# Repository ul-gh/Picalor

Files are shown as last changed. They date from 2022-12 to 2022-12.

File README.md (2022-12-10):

# Picalor

## Multi-Channel Heat Balance Calorimetry on the Raspberry Pi
--> Incomplete - work-in-progress! <--

Thermal power (or heat flow) measurement of one segmented or multiple
individual liquid-cooled or liquid-heated systems under the assumption
that the enthalpy difference of the fluid entering and exiting each system
per unit of time is equal to the energy dissipated or released by the system.

Quasi-isothermal condition can be achieved by using a sufficiently high
flow rate. Accurate heat flow measurements under these conditions
require very sensitive and robust differential temperature sensing.

This is implemented by the Picalor hardware using platinum resistive
temperature sensors in a deflection-type bridge configuration connected
to a multi-channel, high-precision delta-sigma ADC system.

When performing the measurement with fluid temperatures set nearly at
environmental temperature level, convection and radiation heat loss
can be made negligible e.g. for power loss measurements in electronics.

For applications in chemistry, the multi-channel hardware can be useful
for Constant Flux Calorimetry or segmented Continuous Reaction Calorimters.

Supported hardware:

* Picalor OSHW Raspberry Pi add-on circuit board featuring:
    - 16-channel analog frontend for Pt 1000 sensors
    - 4x pulse-timing flow sensor inputs
    - 2x ADS1256 24-Bit 8-ch ADC
* Waveshare "High Precision AD/DA board"

## Hardware:
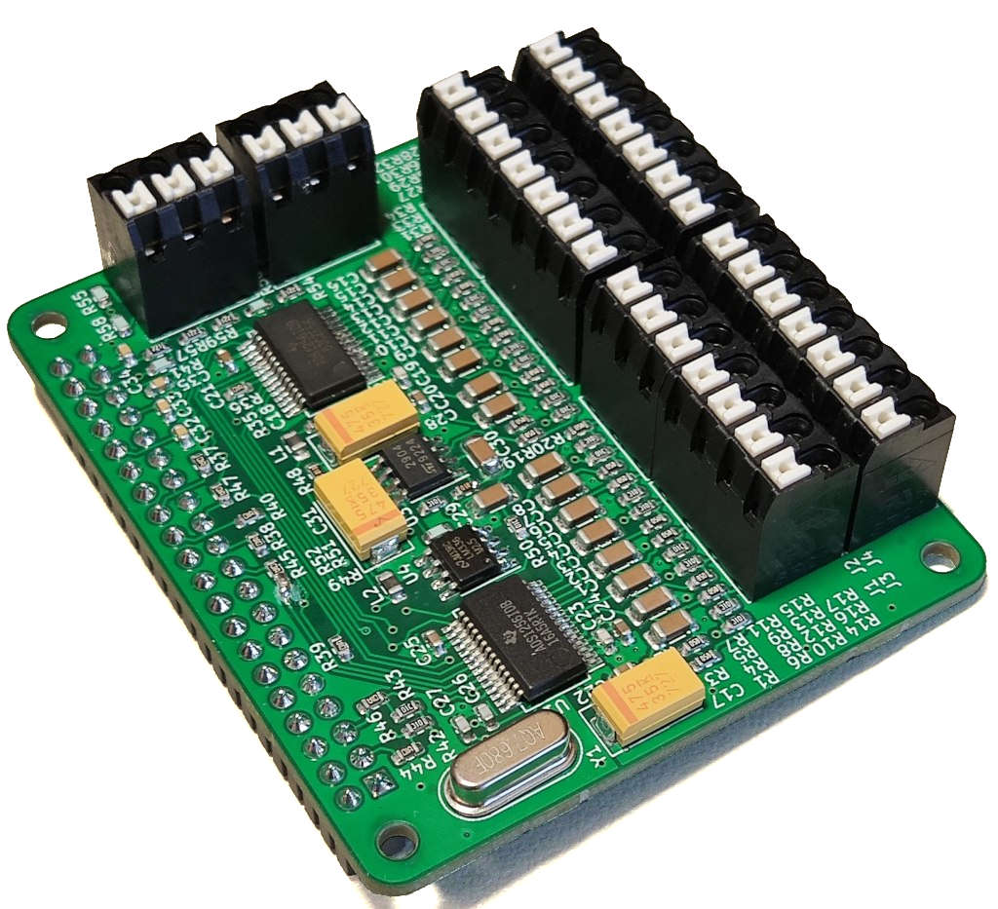
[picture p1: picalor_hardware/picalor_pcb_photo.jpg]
Picalor PCB Photo


* PCB Design Files: [picalor_hardware](picalor_hardware/)
* [Circuit Diagram (PDF)](https://ul-gh.github.io/Picalor/picalor_hardware/picalor_pcb.pdf)
* [Circuit BOM (HTML)](https://ul-gh.github.io/Picalor/picalor_hardware/ibom.html)

## Software Documentation (Generated):
* [Picalor Core (server component)](https://ul-gh.github.io/Picalor/picalor_core/html/namespaces.html)
* [Picalor App (browser client)](https://ul-gh.github.io/Picalor/picalor_app/html/files.html)

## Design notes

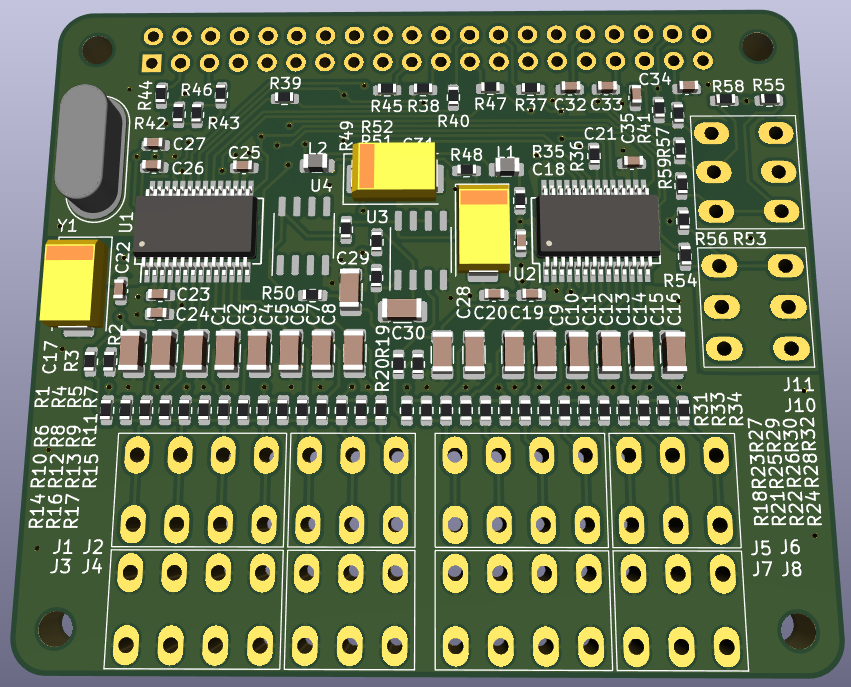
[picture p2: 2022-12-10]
picalor_hardware/circuit_schematics_pcb/picalor_3D_view.png

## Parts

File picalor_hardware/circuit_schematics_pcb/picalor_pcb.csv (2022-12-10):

Source: | D:\Bilanzkalorimeter\isoflux_pcb\isoflux_pcb\isoflux_pcb.kicad_sch
Date: | 18.05.2022 10:55:47
Tool: | Eeschema (6.0.5)
Generator: | C:\Program Files\KiCad\6.0\bin\scripting\plugins/bom_csv_grouped_by_value.py
Component Count: | 113
Individual Components:
Item | Qty | Reference(s) | Value | LibPart | Footprint | Datasheet
 |  | C1 | 1u | Device:C | Capacitor_SMD:C_1206_3216Metric | ~
 |  | C2 | 1u | Device:C | Capacitor_SMD:C_1206_3216Metric | ~
 |  | C3 | 1u | Device:C | Capacitor_SMD:C_1206_3216Metric | ~
 |  | C4 | 1u | Device:C | Capacitor_SMD:C_1206_3216Metric | ~
 |  | C5 | 1u | Device:C | Capacitor_SMD:C_1206_3216Metric | ~
 |  | C6 | 1u | Device:C | Capacitor_SMD:C_1206_3216Metric | ~
 |  | C7 | 1u | Device:C | Capacitor_SMD:C_1206_3216Metric | ~
 |  | C8 | 1u | Device:C | Capacitor_SMD:C_1206_3216Metric | ~
 |  | C9 | 1u | Device:C | Capacitor_SMD:C_1206_3216Metric | ~
 |  | C10 | 1u | Device:C | Capacitor_SMD:C_1206_3216Metric | ~
 |  | C11 | 1u | Device:C | Capacitor_SMD:C_1206_3216Metric | ~
 |  | C12 | 1u | Device:C | Capacitor_SMD:C_1206_3216Metric | ~
 |  | C13 | 1u | Device:C | Capacitor_SMD:C_1206_3216Metric | ~
 |  | C14 | 1u | Device:C | Capacitor_SMD:C_1206_3216Metric | ~
 |  | C15 | 1u | Device:C | Capacitor_SMD:C_1206_3216Metric | ~
 |  | C16 | 1u | Device:C | Capacitor_SMD:C_1206_3216Metric | ~
 |  | C17 | T491D 47U | Device:C_Polarized | Capacitor_Tantalum_SMD:CP_EIA-7343-31_Kemet-D | ~
 |  | C18 | 100n | Device:C | Capacitor_SMD:C_0603_1608Metric | ~
 |  | C19 | 100p | Device:C | Capacitor_SMD:C_0603_1608Metric | ~
 |  | C20 | 100n | Device:C | Capacitor_SMD:C_0603_1608Metric | ~
 |  | C21 | 100n | Device:C | Capacitor_SMD:C_0603_1608Metric | ~
 |  | C22 | 100n | Device:C | Capacitor_SMD:C_0603_1608Metric | ~
 |  | C23 | 100p | Device:C | Capacitor_SMD:C_0603_1608Metric | ~
 |  | C24 | 100n | Device:C | Capacitor_SMD:C_0603_1608Metric | ~
 |  | C25 | 100n | Device:C | Capacitor_SMD:C_0603_1608Metric | ~
 |  | C26 | 47p | Device:C | Capacitor_SMD:C_0603_1608Metric | ~
 |  | C27 | 47p | Device:C | Capacitor_SMD:C_0603_1608Metric | ~
 |  | C28 | T491D 47U | Device:C_Polarized | Capacitor_Tantalum_SMD:CP_EIA-7343-31_Kemet-D | ~
 |  | C29 | 1u | Device:C | Capacitor_SMD:C_1206_3216Metric | ~
 |  | C30 | 1u | Device:C | Capacitor_SMD:C_1206_3216Metric | ~
 |  | C31 | T491D 47U | Device:C_Polarized | Capacitor_Tantalum_SMD:CP_EIA-7343-31_Kemet-D | ~
 |  | C32 | 10n | Device:C | Capacitor_SMD:C_0603_1608Metric | ~
 |  | C33 | 10n | Device:C | Capacitor_SMD:C_0603_1608Metric | ~
 |  | C34 | 10n | Device:C | Capacitor_SMD:C_0603_1608Metric | ~
 |  | C35 | 10n | Device:C | Capacitor_SMD:C_0603_1608Metric | ~
 |  | J1 | AST21304 | Connector:Conn_01x04_Female | lib_ul_mech:TerminalBlock_MetzConnect_AST21304 | ~
 |  | J2 | AST21303 | Connector:Conn_01x03_Female | lib_ul_mech:TerminalBlock_MetzConnect_AST21303 | ~
 |  | J3 | AST21304 | Connector:Conn_01x04_Female | lib_ul_mech:TerminalBlock_MetzConnect_AST21304 | ~
 |  | J4 | AST21303 | Connector:Conn_01x03_Female | lib_ul_mech:TerminalBlock_MetzConnect_AST21303 | ~
 |  | J5 | AST21304 | Connector:Conn_01x04_Female | lib_ul_mech:TerminalBlock_MetzConnect_AST21304 | ~
 |  | J6 | AST21303 | Connector:Conn_01x03_Female | lib_ul_mech:TerminalBlock_MetzConnect_AST21303 | ~
 |  | J7 | AST21304 | Connector:Conn_01x04_Female | lib_ul_mech:TerminalBlock_MetzConnect_AST21304 | ~
 |  | J8 | AST21303 | Connector:Conn_01x03_Female | lib_ul_mech:TerminalBlock_MetzConnect_AST21303 | ~
 |  | J9 | Raspberry_Pi_2_3 | Connector:Raspberry_Pi_2_3 | Connector_PinSocket_2.54mm:PinSocket_2x20_P2.54mm_Vertical | https://www.raspberrypi.org/documentation/hardware/raspberrypi/schematics/rpi_SCH_3bplus_1p0_reduced.pdf
 |  | J10 | AST21303 | Connector:Conn_01x03_Female | lib_ul_mech:TerminalBlock_MetzConnect_AST21303 | ~
 |  | J11 | AST21303 | Connector:Conn_01x03_Female | lib_ul_mech:TerminalBlock_MetzConnect_AST21303 | ~
 |  | L1 | BLM21AG102 | Device:L_Ferrite_Small | Inductor_SMD:L_0805_2012Metric | ~
 |  | L2 | BLM21AG102 | Device:L_Ferrite_Small | Inductor_SMD:L_0805_2012Metric | ~
 |  | NT3 | NetTie_2 | Device:NetTie_2 | NetTie:NetTie-2_SMD_Pad0.5mm | ~
 |  | R1 | 10k | Device:R | Resistor_SMD:R_0603_1608Metric | ~
 |  | R2 | 1k1 | Device:R | Resistor_SMD:R_0603_1608Metric | ~
 |  | R3 | 1k1 | Device:R | Resistor_SMD:R_0603_1608Metric | ~
 |  | R4 | 10k | Device:R | Resistor_SMD:R_0603_1608Metric | ~
 |  | R5 | 1k1 | Device:R | Resistor_SMD:R_0603_1608Metric | ~
 |  | R6 | 10k | Device:R | Resistor_SMD:R_0603_1608Metric | ~
 |  | R7 | 1k1 | Device:R | Resistor_SMD:R_0603_1608Metric | ~
 |  | R8 | 10k | Device:R | Resistor_SMD:R_0603_1608Metric | ~
 |  | R9 | 1k1 | Device:R | Resistor_SMD:R_0603_1608Metric | ~
 |  | R10 | 10k | Device:R | Resistor_SMD:R_0603_1608Metric | ~
 |  | R11 | 1k1 | Device:R | Resistor_SMD:R_0603_1608Metric | ~
 |  | R12 | 10k | Device:R | Resistor_SMD:R_0603_1608Metric | ~
 |  | R13 | 1k1 | Device:R | Resistor_SMD:R_0603_1608Metric | ~
 |  | R14 | 10k | Device:R | Resistor_SMD:R_0603_1608Metric | ~
 |  | R15 | 1k1 | Device:R | Resistor_SMD:R_0603_1608Metric | ~
 |  | R16 | 10k | Device:R | Resistor_SMD:R_0603_1608Metric | ~
 |  | R17 | 1k1 | Device:R | Resistor_SMD:R_0603_1608Metric | ~
 |  | R18 | 10k | Device:R | Resistor_SMD:R_0603_1608Metric | ~
 |  | R19 | 1k1 | Device:R | Resistor_SMD:R_0603_1608Metric | ~
 |  | R20 | 1k1 | Device:R | Resistor_SMD:R_0603_1608Metric | ~
 |  | R21 | 10k | Device:R | Resistor_SMD:R_0603_1608Metric | ~
 |  | R22 | 1k1 | Device:R | Resistor_SMD:R_0603_1608Metric | ~
 |  | R23 | 10k | Device:R | Resistor_SMD:R_0603_1608Metric | ~
 |  | R24 | 1k1 | Device:R | Resistor_SMD:R_0603_1608Metric | ~
 |  | R25 | 10k | Device:R | Resistor_SMD:R_0603_1608Metric | ~
 |  | R26 | 1k1 | Device:R | Resistor_SMD:R_0603_1608Metric | ~
 |  | R27 | 10k | Device:R | Resistor_SMD:R_0603_1608Metric | ~
 |  | R28 | 1k1 | Device:R | Resistor_SMD:R_0603_1608Metric | ~
 |  | R29 | 10k | Device:R | Resistor_SMD:R_0603_1608Metric | ~
 |  | R30 | 1k1 | Device:R | Resistor_SMD:R_0603_1608Metric | ~
 |  | R31 | 10k | Device:R | Resistor_SMD:R_0603_1608Metric | ~
 |  | R32 | 1k1 | Device:R | Resistor_SMD:R_0603_1608Metric | ~
 |  | R33 | 10k | Device:R | Resistor_SMD:R_0603_1608Metric | ~
 |  | R34 | 1k1 | Device:R | Resistor_SMD:R_0603_1608Metric | ~
 |  | R35 | 10 | Device:R | Resistor_SMD:R_0603_1608Metric | ~
 |  | R36 | 100 | Device:R | Resistor_SMD:R_0603_1608Metric | ~
 |  | R37 | 100 | Device:R | Resistor_SMD:R_0603_1608Metric | ~
 |  | R38 | 100 | Device:R | Resistor_SMD:R_0603_1608Metric | ~
 |  | R39 | 100 | Device:R | Resistor_SMD:R_0603_1608Metric | ~
 |  | R40 | 100 | Device:R | Resistor_SMD:R_0603_1608Metric | ~
 |  | R41 | 2k2 | Device:R | Resistor_SMD:R_0603_1608Metric | ~
 |  | R42 | 10k | Device:R | Resistor_SMD:R_0603_1608Metric | ~
 |  | R43 | 10k | Device:R | Resistor_SMD:R_0603_1608Metric | ~
 |  | R44 | 100 | Device:R | Resistor_SMD:R_0603_1608Metric | ~
 |  | R45 | 100 | Device:R | Resistor_SMD:R_0603_1608Metric | ~
 |  | R46 | 100 | Device:R | Resistor_SMD:R_0603_1608Metric | ~
 |  | R47 | 100 | Device:R | Resistor_SMD:R_0603_1608Metric | ~
 |  | R48 | 10 | Device:R | Resistor_SMD:R_0603_1608Metric | ~
 |  | R49 | 2k2 | Device:R | Resistor_SMD:R_0603_1608Metric | ~
 |  | R50 | 10k | Device:R | Resistor_SMD:R_0603_1608Metric | ~
 |  | R51 | 10 | Device:R | Resistor_SMD:R_0603_1608Metric | ~
 |  | R52 | 10k | Device:R | Resistor_SMD:R_0603_1608Metric | ~
 |  | R53 | 2k2 | Device:R | Resistor_SMD:R_0603_1608Metric | ~
 |  | R54 | 220 | Device:R | Resistor_SMD:R_0603_1608Metric | ~
 |  | R55 | 2k2 | Device:R | Resistor_SMD:R_0603_1608Metric | ~
 |  | R56 | 220 | Device:R | Resistor_SMD:R_0603_1608Metric | ~
 |  | R57 | 220 | Device:R | Resistor_SMD:R_0603_1608Metric | ~
 |  | R58 | 2k2 | Device:R | Resistor_SMD:R_0603_1608Metric | ~
 |  | R59 | 220 | Device:R | Resistor_SMD:R_0603_1608Metric | ~
 |  | U1 | ADS1256IDB | lib_ul:ADS1256IDB | Package_SO:SSOP-28_5.3x10.2mm_P0.65mm | https://www.ti.com/lit/gpn/ads1255
 |  | U2 | ADS1256IDB | lib_ul:ADS1256IDB | Package_SO:SSOP-28_5.3x10.2mm_P0.65mm | https://www.ti.com/lit/gpn/ads1255
 |  | U3 | LM358 | Amplifier_Operational:LM358 | Package_SO:SO-8_3.9x4.9mm_P1.27mm | http://www.ti.com/lit/ds/symlink/lm2904-n.pdf
 |  | U4 | LM336BM-2.5 | lib_ul:LM336BM-2.5 | Package_SO:SO-8_3.9x4.9mm_P1.27mm | https://www.ti.com/lit/ds/symlink/lm336-2.5-n.pdf
 |  | Y1 | 7.68M | Device:Crystal_Small | Crystal:Crystal_HC49-4H_Vertical | ~
Collated Components:
Item | Qty | Reference(s) | Value | LibPart | Footprint | Datasheet
1 | 18 | C1, C2, C3, C4, C5, C6, C7, C8, C9, C10, C11, C12, C13, C14, C15, C16, C29, C30 | 1u | Device:C | Capacitor_SMD:C_1206_3216Metric | ~
2 | 3 | C17, C28, C31 | T491D 47U | Device:C_Polarized | Capacitor_Tantalum_SMD:CP_EIA-7343-31_Kemet-D | ~
3 | 6 | C18, C20, C21, C22, C24, C25 | 100n | Device:C | Capacitor_SMD:C_0603_1608Metric | ~
4 | 2 | C19, C23 | 100p | Device:C | Capacitor_SMD:C_0603_1608Metric | ~
5 | 2 | C26, C27 | 47p | Device:C | Capacitor_SMD:C_0603_1608Metric | ~
6 | 4 | C32, C33, C34, C35 | 10n | Device:C | Capacitor_SMD:C_0603_1608Metric | ~
7 | 4 | J1, J3, J5, J7 | AST21304 | Connector:Conn_01x04_Female | lib_ul_mech:TerminalBlock_MetzConnect_AST21304 | ~
8 | 6 | J2, J4, J6, J8, J10, J11 | AST21303 | Connector:Conn_01x03_Female | lib_ul_mech:TerminalBlock_MetzConnect_AST21303 | ~
9 | 1 | J9 | Raspberry_Pi_2_3 | Connector:Raspberry_Pi_2_3 | Connector_PinSocket_2.54mm:PinSocket_2x20_P2.54mm_Vertical | https://www.raspberrypi.org/documentation/hardware/raspberrypi/schematics/rpi_SCH_3bplus_1p0_reduced.pdf
10 | 2 | L1, L2 | BLM21AG102 | Device:L_Ferrite_Small | Inductor_SMD:L_0805_2012Metric | ~
11 | 1 | NT3 | NetTie_2 | Device:NetTie_2 | NetTie:NetTie-2_SMD_Pad0.5mm | ~
12 | 20 | R1, R4, R6, R8, R10, R12, R14, R16, R18, R21, R23, R25, R27, R29, R31, R33, R42, R43, R50, R52 | 10k | Device:R | Resistor_SMD:R_0603_1608Metric | ~
13 | 18 | R2, R3, R5, R7, R9, R11, R13, R15, R17, R19, R20, R22, R24, R26, R28, R30, R32, R34 | 1k1 | Device:R | Resistor_SMD:R_0603_1608Metric | ~
14 | 3 | R35, R48, R51 | 10 | Device:R | Resistor_SMD:R_0603_1608Metric | ~
15 | 9 | R36, R37, R38, R39, R40, R44, R45, R46, R47 | 100 | Device:R | Resistor_SMD:R_0603_1608Metric | ~
16 | 5 | R41, R49, R53, R55, R58 | 2k2 | Device:R | Resistor_SMD:R_0603_1608Metric | ~
17 | 4 | R54, R56, R57, R59 | 220 | Device:R | Resistor_SMD:R_0603_1608Metric | ~
18 | 2 | U1, U2 | ADS1256IDB | lib_ul:ADS1256IDB | Package_SO:SSOP-28_5.3x10.2mm_P0.65mm | https://www.ti.com/lit/gpn/ads1255
19 | 1 | U3 | LM358 | Amplifier_Operational:LM358 | Package_SO:SO-8_3.9x4.9mm_P1.27mm | http://www.ti.com/lit/ds/symlink/lm2904-n.pdf
20 | 1 | U4 | LM336BM-2.5 | lib_ul:LM336BM-2.5 | Package_SO:SO-8_3.9x4.9mm_P1.27mm | https://www.ti.com/lit/ds/symlink/lm336-2.5-n.pdf
21 | 1 | Y1 | 7.68M | Device:Crystal_Small | Crystal:Crystal_HC49-4H_Vertical | ~

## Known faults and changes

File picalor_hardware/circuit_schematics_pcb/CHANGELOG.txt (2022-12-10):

V. 0.2		Initial development prototype with PCB
V. 0.2.1	Bugfix release, fix unrouted trace on MOSI
                + move AGND-DGND bridge away from underneath ADC

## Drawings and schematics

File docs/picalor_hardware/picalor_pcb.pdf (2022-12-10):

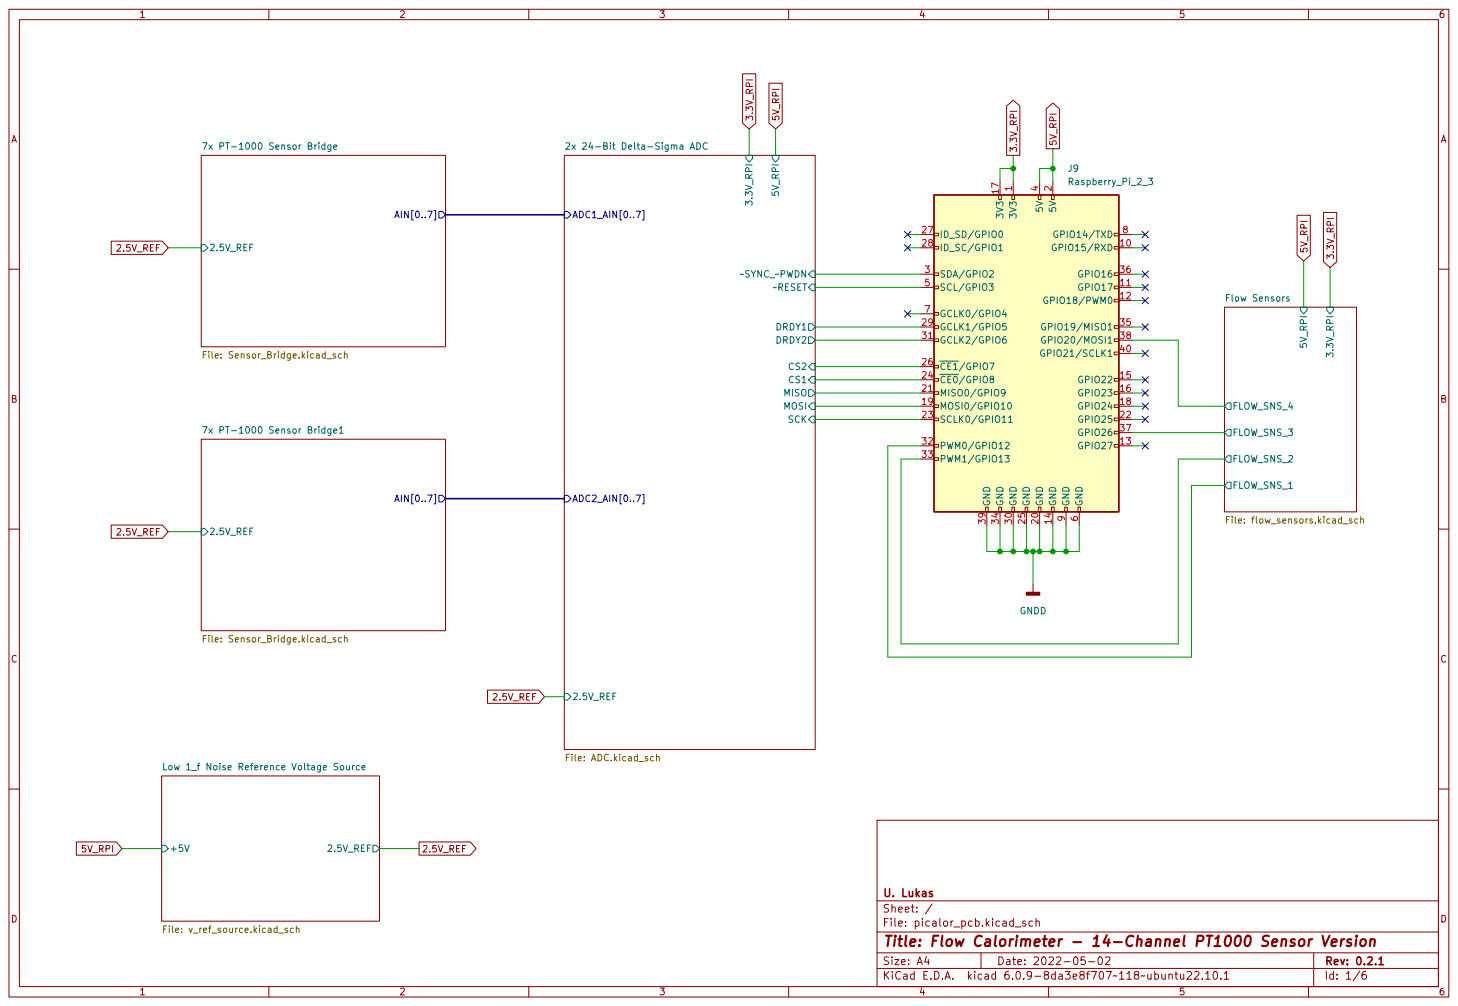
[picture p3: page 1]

2x 24-Bit Delta-Sigma ADC

Low 1_f Noise Reference Voltage Source File: v_ref_source.kicad_sch

Id: 1/6 Title: Flow Calorimeter - 14-Channel PT1000 Sensor Version

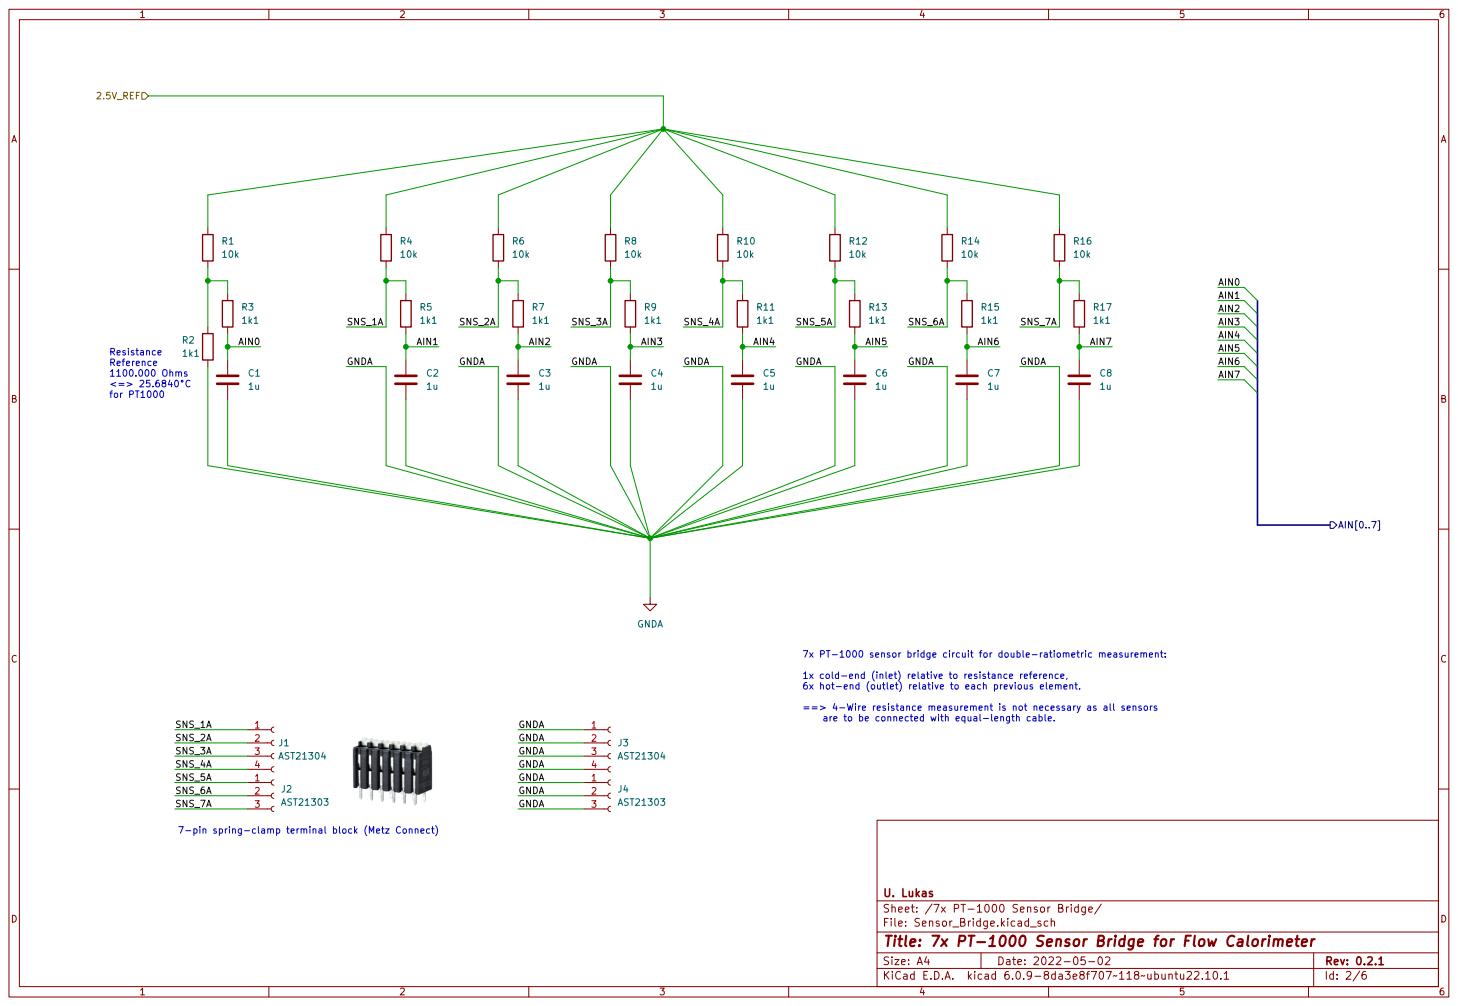
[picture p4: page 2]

7x PT-1000 sensor bridge circuit for double-ratiometric measurement:

1x cold-end (inlet) relative to resistance reference,
6x hot-end (outlet) relative to each previous element.

==> 4-Wire resistance measurement is not necessary as all sensors
are to be connected with equal-length cable.

7-pin spring-clamp terminal block (Metz Connect)

Sheet: /7x PT-1000 Sensor Bridge/ U. Lukas

File: Sensor_Bridge.kicad_sch
Id: 2/6 Title: 7x PT-1000 Sensor Bridge for Flow Calorimeter

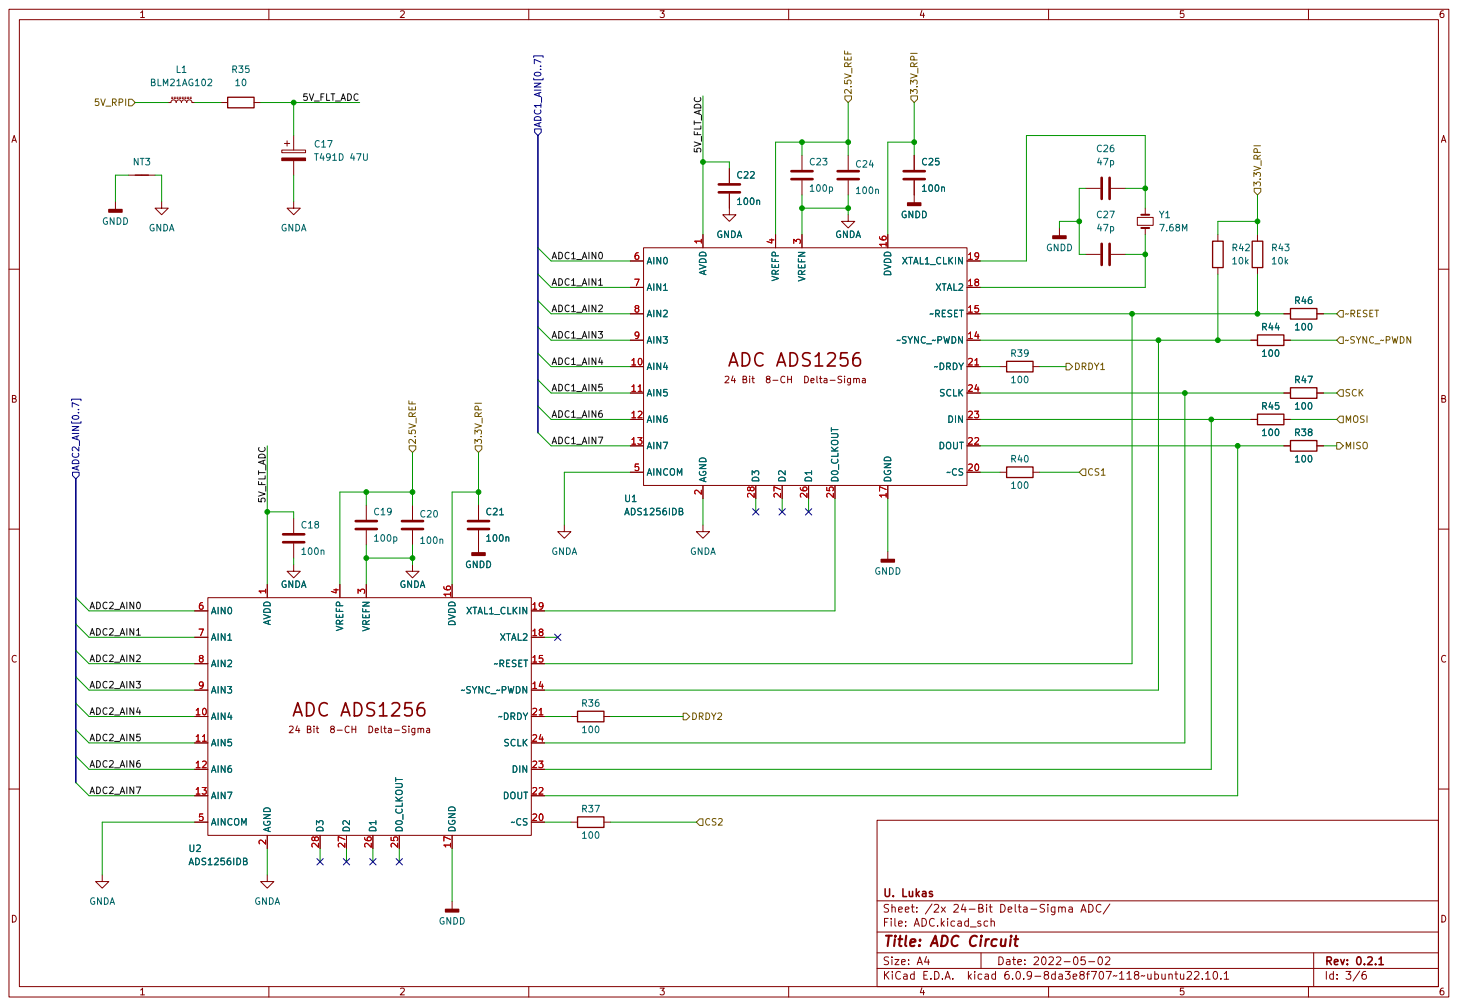
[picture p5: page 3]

2 ~CS20 ~DRDY21 DOUT 22 DIN 23 SCLK 24 D0_CLKOUT 25 D1 26 D2 27 D3 28 VREFN
ADC ADS1256 AVDD

24 Bit 8-CH Delta-Sigma

Sheet: /2x 24-Bit Delta-Sigma ADC/ U. Lukas GNDA

File: ADC.kicad_sch
Id: 3/6 Title: ADC Circuit

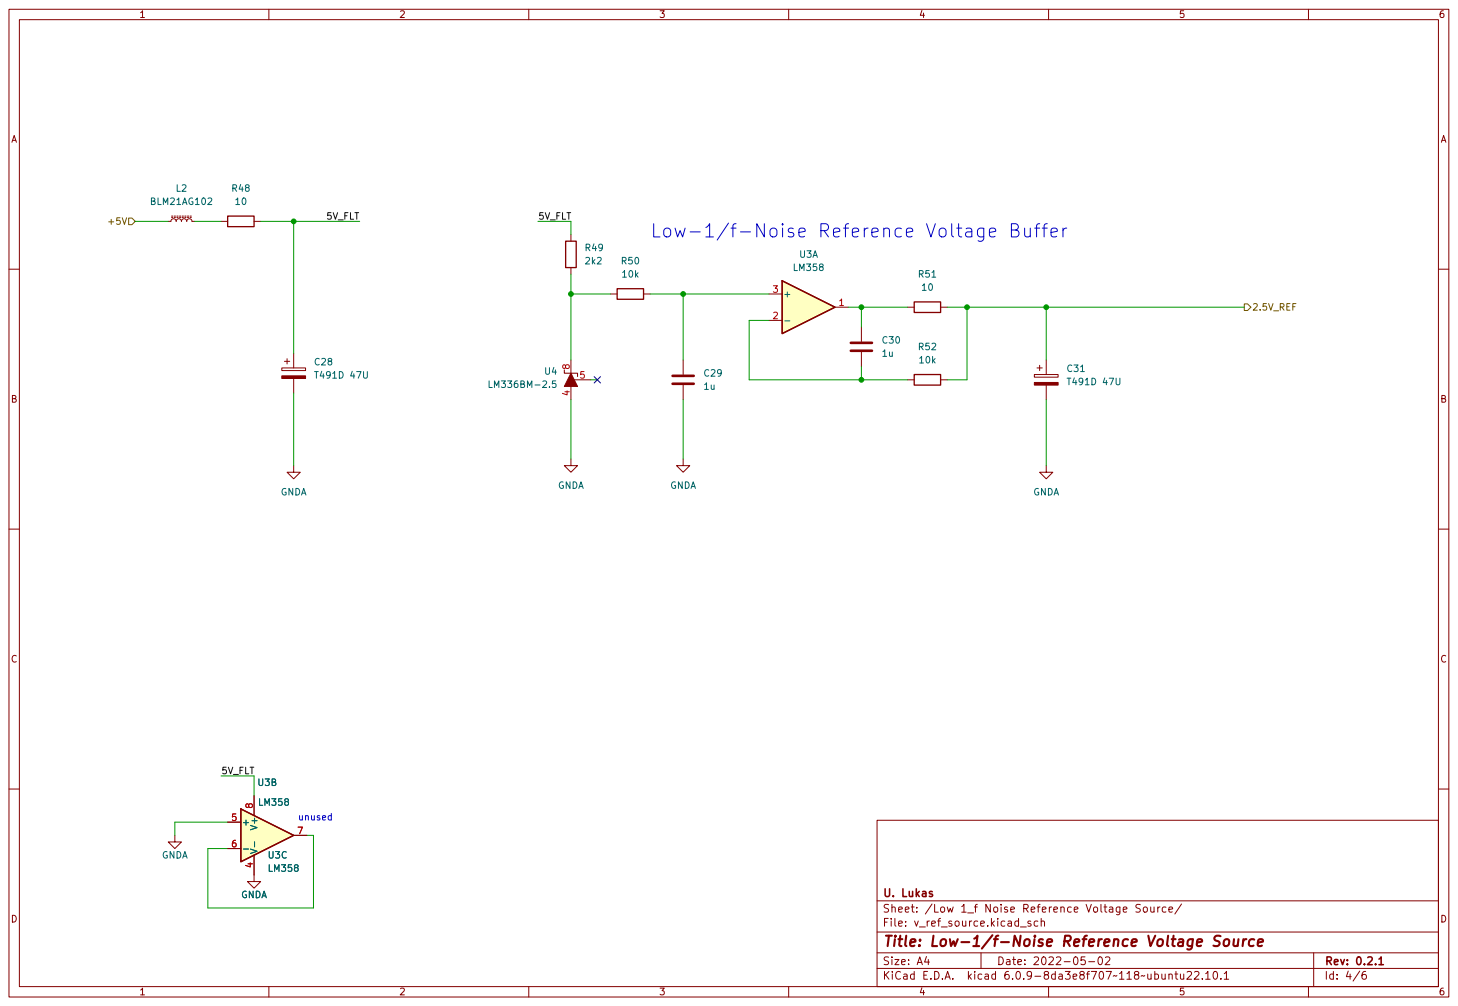
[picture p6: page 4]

Sheet: /Low 1_f Noise Reference Voltage Source/ U. Lukas

File: v_ref_source.kicad_sch
Id: 4/6 Title: Low-1/f-Noise Reference Voltage Source

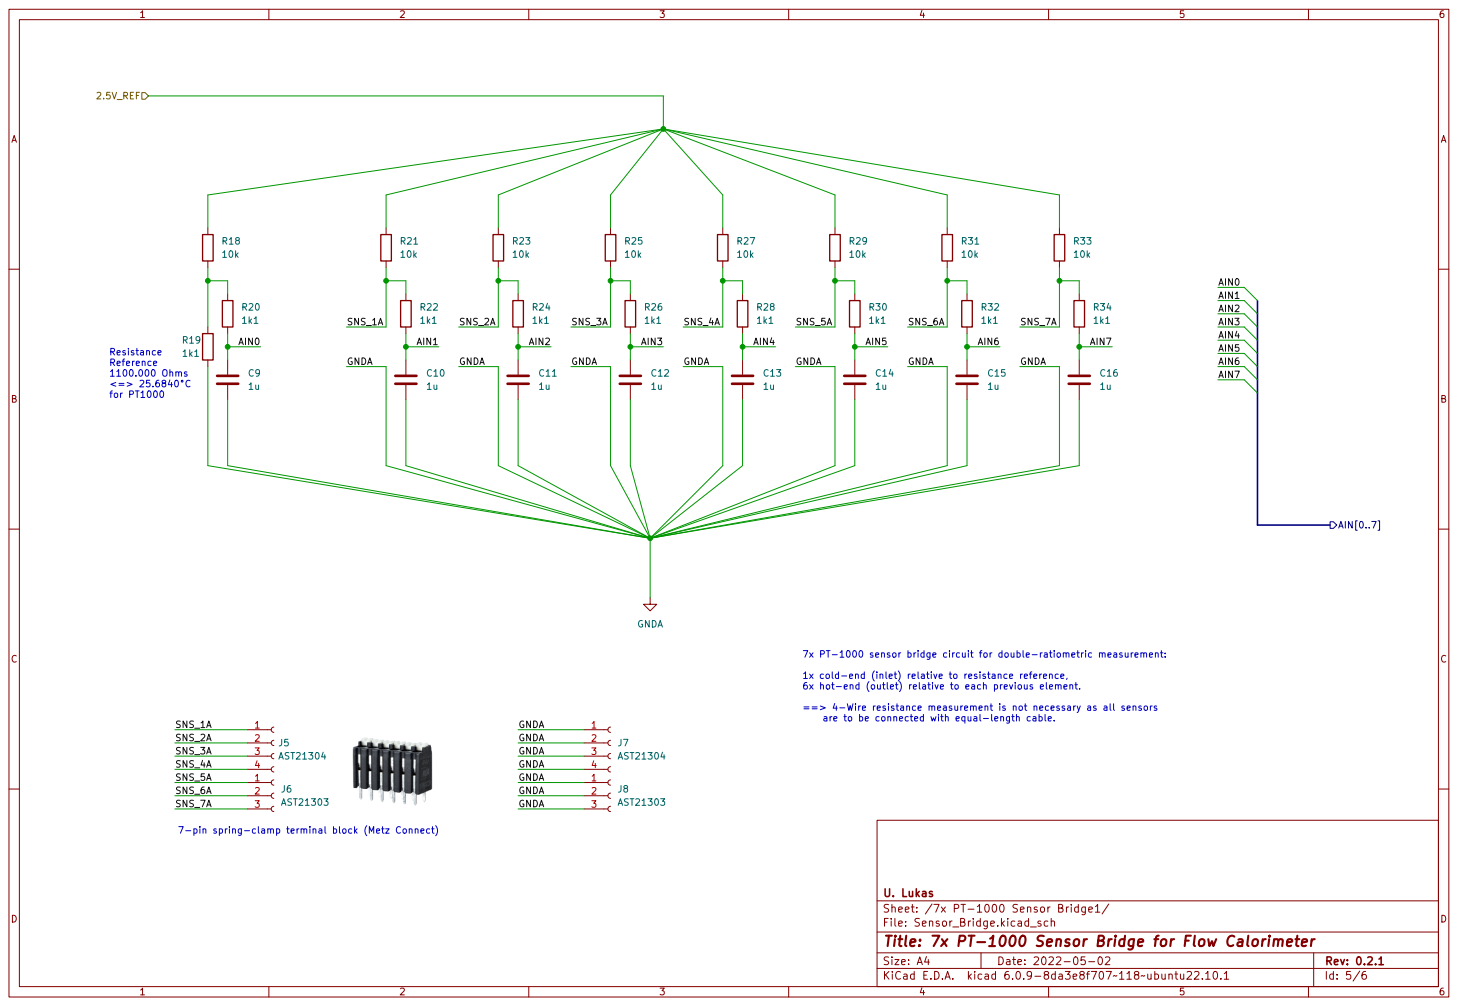
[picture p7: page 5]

7x PT-1000 sensor bridge circuit for double-ratiometric measurement:

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

7-pin spring-clamp terminal block (Metz Connect)

Sheet: /7x PT-1000 Sensor Bridge1/ U. Lukas

File: Sensor_Bridge.kicad_sch
Id: 5/6 Title: 7x PT-1000 Sensor Bridge for Flow Calorimeter

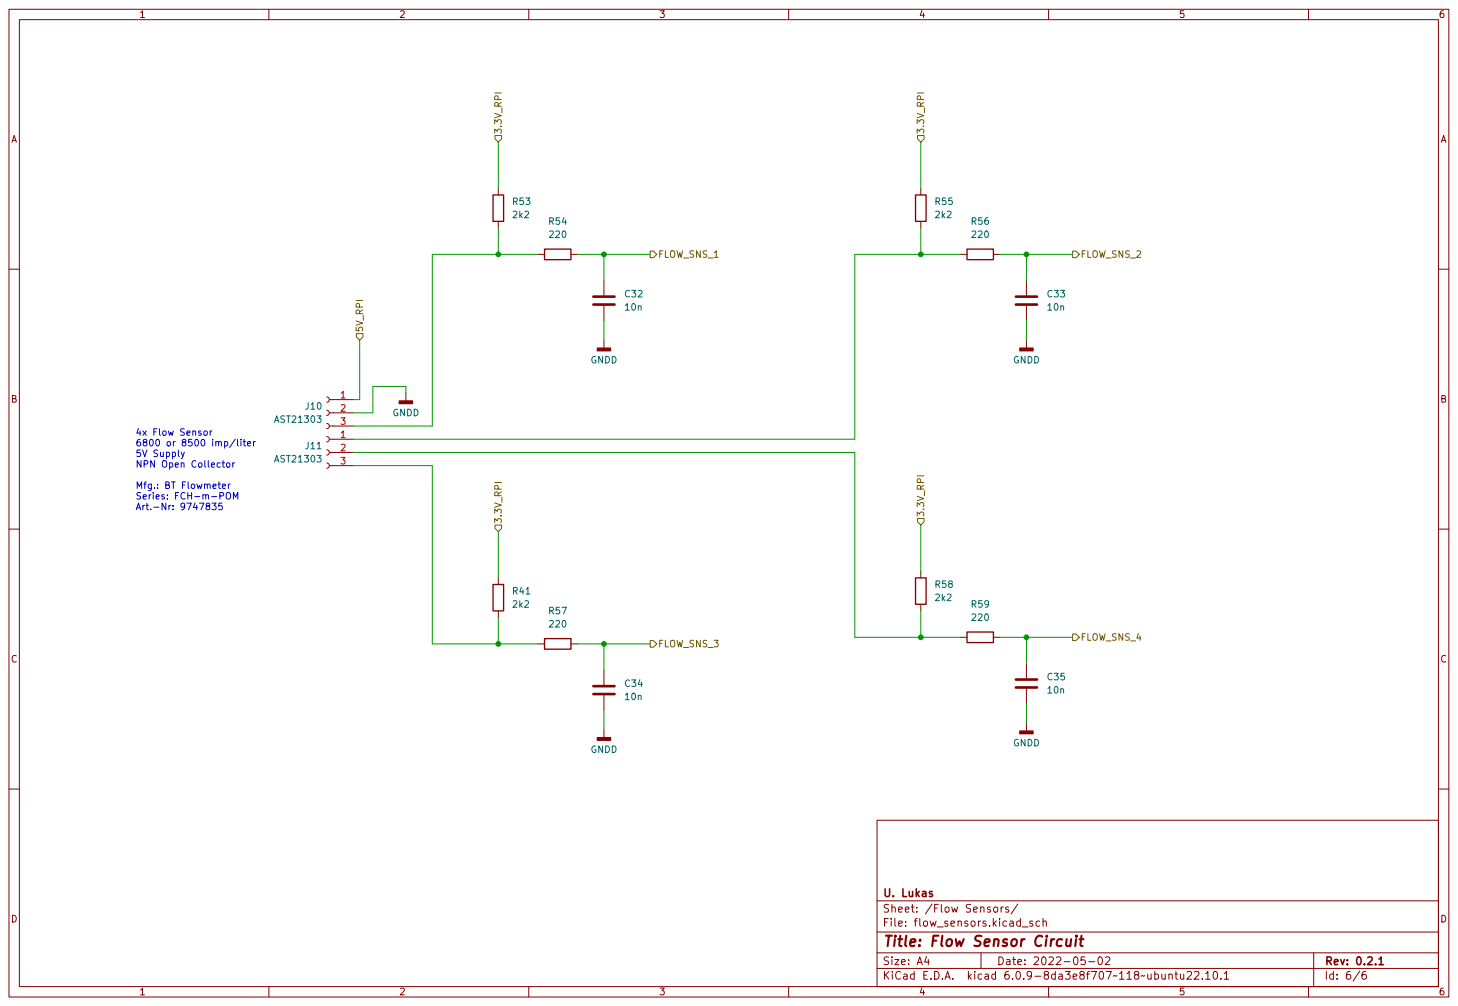
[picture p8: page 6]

4x Flow Sensor 6800 or 8500 imp/liter

Mfg.: BT Flowmeter Series: FCH-m-POM

File: flow_sensors.kicad_sch Sheet: /Flow Sensors/ U. Lukas

Id: 6/6 Title: Flow Sensor Circuit

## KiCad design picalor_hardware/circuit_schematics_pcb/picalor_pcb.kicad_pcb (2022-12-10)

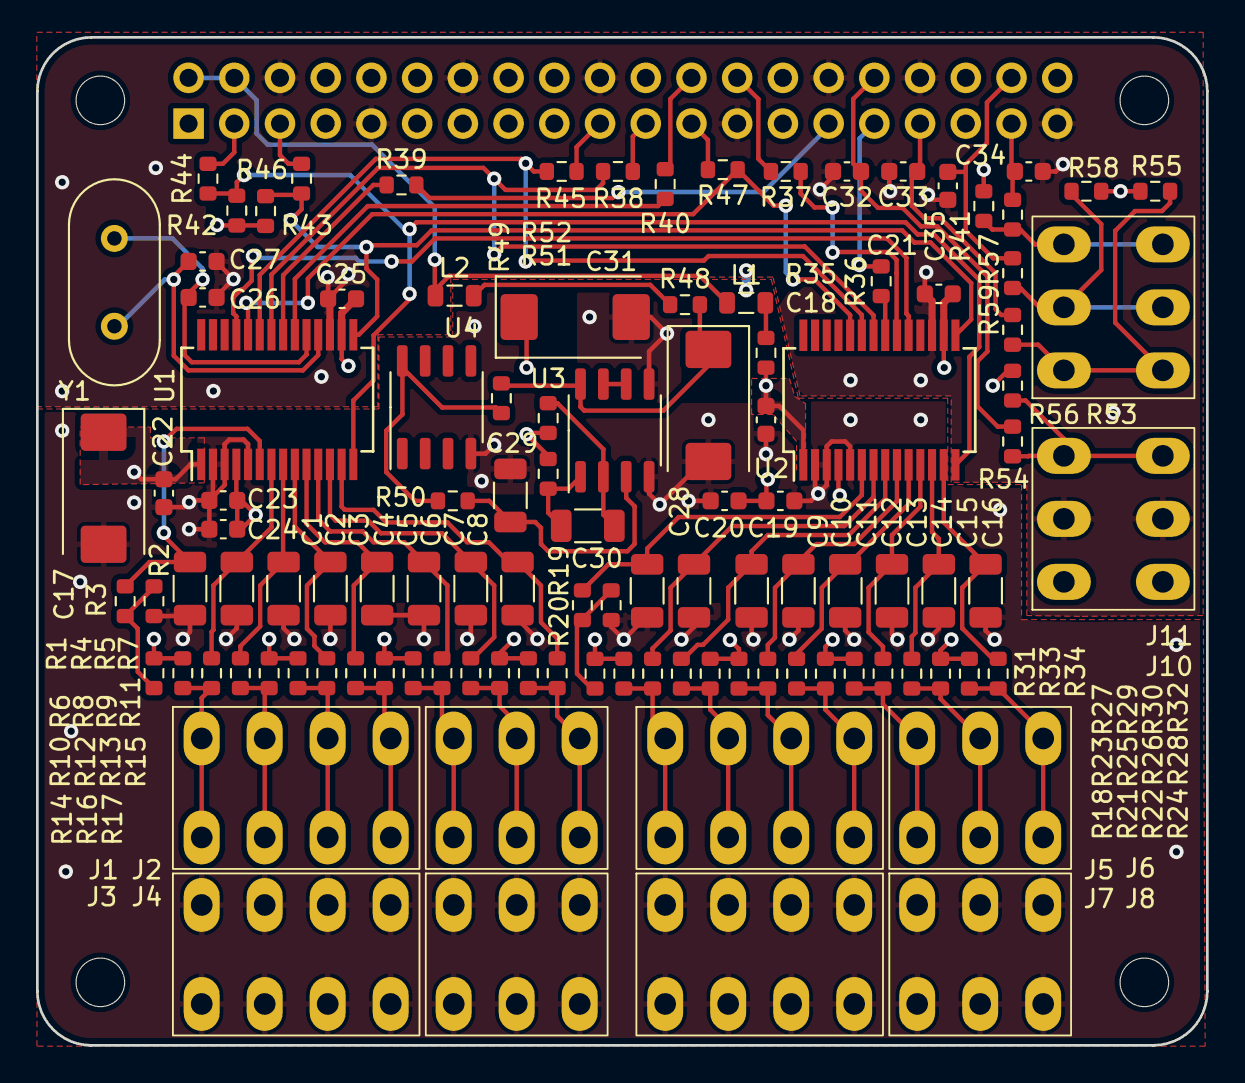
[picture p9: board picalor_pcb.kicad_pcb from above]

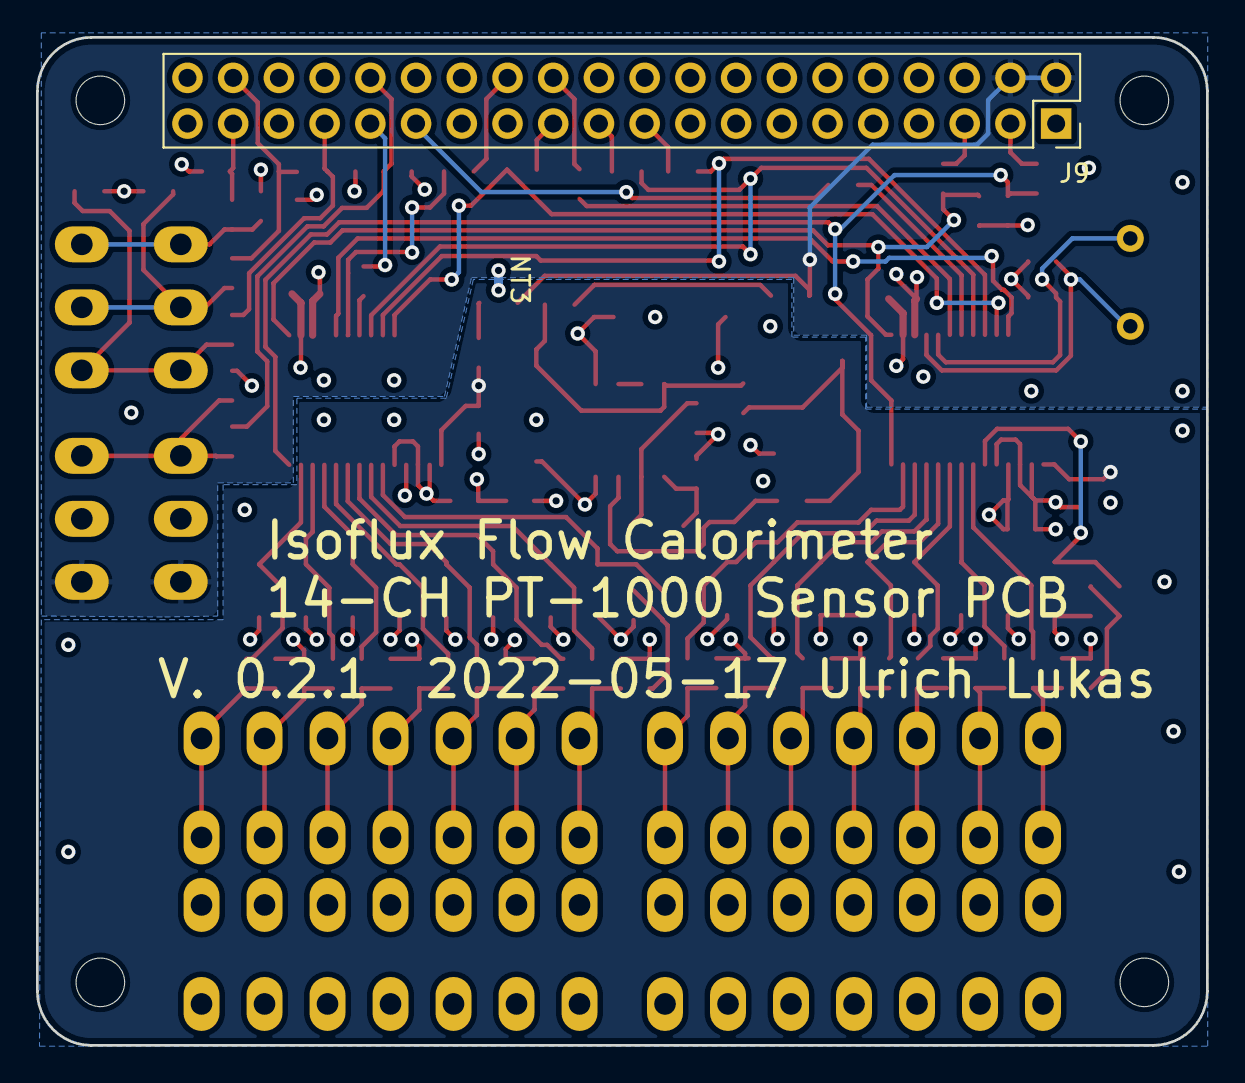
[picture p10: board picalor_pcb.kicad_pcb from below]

Board: 4 copper layers, 65.0 x 56.0 mm, 117 parts (2 on the bottom side), 75 nets.

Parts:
C1, C2, C3, C4, C5, C6, C7, C8, C9, C10, C11, C12, C13, C14, C15, C16, C29, C30: 1u; C_1206_3216Metric
C17, C28, C31: T491D 47U; CP_EIA-7343-31_Kemet-D
C18, C20, C21, C22, C24, C25: 100n; C_0603_1608Metric
C19, C23: 100p; C_0603_1608Metric
C26, C27: 47p; C_0603_1608Metric
C32, C33, C34, C35: 10n; C_0603_1608Metric
J1, J3, J5, J7: AST21304; TerminalBlock_MetzConnect_AST21304
J2, J4, J6, J8, J10, J11: AST21303; TerminalBlock_MetzConnect_AST21303
J9: Raspberry_Pi_2_3; PinSocket_2x20_P2.54mm_Vertical
L1, L2: BLM21AG102; L_0805_2012Metric
M1, M2, M3, M4: MountingHole_2.7mm_M2.5
NT3: NetTie_2; NetTie-2_SMD_Pad0.5mm
R1, R4, R6, R8, R10, R12, R14, R16, R18, R21, R23, R25, R27, R29, R31, R33, R42, R43, R50, R52: 10k; R_0603_1608Metric
R2, R3, R5, R7, R9, R11, R13, R15, R17, R19, R20, R22, R24, R26, R28, R30, R32, R34: 1k1; R_0603_1608Metric
R35, R48, R51: 10; R_0603_1608Metric
R36, R37, R38, R39, R40, R44, R45, R46, R47: 100; R_0603_1608Metric
R41, R49, R53, R55, R58: 2k2; R_0603_1608Metric
R54, R56, R57, R59: 220; R_0603_1608Metric
U1, U2: ADS1256IDB; SSOP-28_5.3x10.2mm_P0.65mm
U3: LM358; SO-8_3.9x4.9mm_P1.27mm
U4: LM336BM-2.5; SO-8_3.9x4.9mm_P1.27mm
Y1: 7.68M; Crystal_HC49-4H_Vertical

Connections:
2.5V_REF: C19.1, C20.1, C23.1, C24.1, C31.1, R1.1, R4.1, R6.1, R8.1, R10.1, R12.1, R14.1, R16.1, R18.1, R21.1, R23.1, R25.1, R27.1, R29.1, R31.1, R33.1, R51.2, R52.2, U1.4 (VREFP), U2.4 (VREFP)
3.3V_RPI: C21.1, C25.1, J9.1 (3V3), J9.17 (3V3), R41.1, R42.2, R43.2, R53.1, R55.1, R58.1, U1.16 (DVDD), U2.16 (DVDD)
5V_RPI: J9.2 (5V), J9.4 (5V), J10.1, L1.1, L2.1
/2x 24-Bit Delta-Sigma ADC/5V_FLT_ADC: C17.1, C18.1, C22.1, R35.2, U1.1 (AVDD), U2.1 (AVDD)
/2x 24-Bit Delta-Sigma ADC/ADC1_AIN0: C1.1, R3.2, U1.6 (AIN0)
/2x 24-Bit Delta-Sigma ADC/ADC1_AIN1: C2.1, R5.2, U1.7 (AIN1)
/2x 24-Bit Delta-Sigma ADC/ADC1_AIN2: C3.1, R7.2, U1.8 (AIN2)
/2x 24-Bit Delta-Sigma ADC/ADC1_AIN3: C4.1, R9.2, U1.9 (AIN3)
/2x 24-Bit Delta-Sigma ADC/ADC1_AIN4: C5.1, R11.2, U1.10 (AIN4)
/2x 24-Bit Delta-Sigma ADC/ADC1_AIN5: C6.1, R13.2, U1.11 (AIN5)
/2x 24-Bit Delta-Sigma ADC/ADC1_AIN6: C7.1, R15.2, U1.12 (AIN6)
/2x 24-Bit Delta-Sigma ADC/ADC1_AIN7: C8.1, R17.2, U1.13 (AIN7)
/2x 24-Bit Delta-Sigma ADC/ADC2_AIN0: C9.1, R20.2, U2.6 (AIN0)
/2x 24-Bit Delta-Sigma ADC/ADC2_AIN1: C10.1, R22.2, U2.7 (AIN1)
/2x 24-Bit Delta-Sigma ADC/ADC2_AIN2: C11.1, R24.2, U2.8 (AIN2)
/2x 24-Bit Delta-Sigma ADC/ADC2_AIN3: C12.1, R26.2, U2.9 (AIN3)
/2x 24-Bit Delta-Sigma ADC/ADC2_AIN4: C13.1, R28.2, U2.10 (AIN4)
/2x 24-Bit Delta-Sigma ADC/ADC2_AIN5: C14.1, R30.2, U2.11 (AIN5)
/2x 24-Bit Delta-Sigma ADC/ADC2_AIN6: C15.1, R32.2, U2.12 (AIN6)
/2x 24-Bit Delta-Sigma ADC/ADC2_AIN7: C16.1, R34.2, U2.13 (AIN7)
/2x 24-Bit Delta-Sigma ADC/CS1: J9.24 (~CE0/GPIO8), R40.2
/2x 24-Bit Delta-Sigma ADC/CS2: J9.26 (~CE1/GPIO7), R37.2
/2x 24-Bit Delta-Sigma ADC/DRDY1: J9.29 (GCLK1/GPIO5), R39.2
/2x 24-Bit Delta-Sigma ADC/DRDY2: J9.31 (GCLK2/GPIO6), R36.2
/2x 24-Bit Delta-Sigma ADC/MISO: J9.21 (MISO0/GPIO9), R38.2
/2x 24-Bit Delta-Sigma ADC/MOSI: J9.19 (MOSI0/GPIO10), R45.2
/2x 24-Bit Delta-Sigma ADC/SCK: J9.23 (SCLK0/GPIO11), R47.2
/2x 24-Bit Delta-Sigma ADC/~RESET: J9.5 (SCL/GPIO3), R46.2
/2x 24-Bit Delta-Sigma ADC/~SYNC_~PWDN: J9.3 (SDA/GPIO2), R44.2
/7x PT-1000 Sensor Bridge1/SNS_1A: J5.1, R21.2, R22.1
/7x PT-1000 Sensor Bridge1/SNS_2A: J5.2, R23.2, R24.1
/7x PT-1000 Sensor Bridge1/SNS_3A: J5.3, R25.2, R26.1
/7x PT-1000 Sensor Bridge1/SNS_4A: J5.4, R27.2, R28.1
/7x PT-1000 Sensor Bridge1/SNS_5A: J6.1, R29.2, R30.1
/7x PT-1000 Sensor Bridge1/SNS_6A: J6.2, R31.2, R32.1
/7x PT-1000 Sensor Bridge1/SNS_7A: J6.3, R33.2, R34.1
/7x PT-1000 Sensor Bridge/SNS_1A: J1.1, R4.2, R5.1
/7x PT-1000 Sensor Bridge/SNS_2A: J1.2, R6.2, R7.1
/7x PT-1000 Sensor Bridge/SNS_3A: J1.3, R8.2, R9.1
/7x PT-1000 Sensor Bridge/SNS_4A: J1.4, R10.2, R11.1
/7x PT-1000 Sensor Bridge/SNS_5A: J2.1, R12.2, R13.1
/7x PT-1000 Sensor Bridge/SNS_6A: J2.2, R14.2, R15.1
/7x PT-1000 Sensor Bridge/SNS_7A: J2.3, R16.2, R17.1
/Flow Sensors/FLOW_SNS_1: C32.1, J9.32 (PWM0/GPIO12), R54.1
/Flow Sensors/FLOW_SNS_2: C33.1, J9.33 (PWM1/GPIO13), R56.1
/Flow Sensors/FLOW_SNS_3: C34.1, J9.37 (GPIO26), R57.1
/Flow Sensors/FLOW_SNS_4: C35.1, J9.38 (GPIO20/MOSI1), R59.1
/Low 1_f Noise Reference Voltage Source/5V_FLT: C28.1, R48.2, R49.1, U3.8 (V+)
GNDA: C1.2, C2.2, C3.2, C4.2, C5.2, C6.2, C7.2, C8.2, C9.2, C10.2, C11.2, C12.2, C13.2, C14.2, C15.2, C16.2, C17.2, C18.2, C19.2, C20.2, C22.2, C23.2, C24.2, C28.2, C29.2, C31.2, J3.1, J3.2, J3.3, J3.4, J4.1, J4.2, J4.3, J7.1, J7.2, J7.3, J7.4, J8.1, J8.2, J8.3, NT3.2, R2.2, R19.2, U1.2 (AGND), U1.3 (VREFN), U1.5 (AINCOM), U2.2 (AGND), U2.3 (VREFN), U2.5 (AINCOM), U3.4 (V-), U3.5 (+), U4.4 (A)
GNDD: C21.2, C25.2, C26.1, C27.1, C32.2, C33.2, C34.2, C35.2, J9.6 (GND), J9.9 (GND), J9.14 (GND), J9.20 (GND), J9.25 (GND), J9.30 (GND), J9.34 (GND), J9.39 (GND), J10.2, NT3.1, U1.17 (DGND), U2.17 (DGND)
unnamed: C26.2, U1.19 (XTAL1_CLKIN), Y1.2
unnamed: C27.2, U1.18 (XTAL2), Y1.1
unnamed: C29.1, R50.2, U3.3 (+)
unnamed: C30.1, R51.1, U3.1
unnamed: C30.2, R52.1, U3.2 (-)
unnamed: J10.3, R53.2, R54.2
unnamed: J11.1, R55.2, R56.2
unnamed: J11.2, R58.2, R59.2
unnamed: J11.3, R41.2, R57.2
unnamed: L1.2, R35.1
unnamed: L2.2, R48.1
unnamed: R1.2, R2.1, R3.1
unnamed: R18.2, R19.1, R20.1
unnamed: R36.1, U2.21 (~DRDY)
unnamed: R37.1, U2.20 (~CS)
unnamed: R38.1, U1.22 (DOUT), U2.22 (DOUT)
unnamed: R39.1, U1.21 (~DRDY)
unnamed: R40.1, U1.20 (~CS)
unnamed: R42.1, R44.1, U1.14 (~SYNC_~PWDN), U2.14 (~SYNC_~PWDN)
unnamed: R43.1, R46.1, U1.15 (~RESET), U2.15 (~RESET)
unnamed: R45.1, U1.23 (DIN), U2.23 (DIN)
unnamed: R47.1, U1.24 (SCLK), U2.24 (SCLK)
unnamed: R49.2, R50.1, U4.8 (K)
unnamed: U1.25 (D0_CLKOUT), U2.19 (XTAL1_CLKIN)
unnamed: U3.6 (-), U3.7
